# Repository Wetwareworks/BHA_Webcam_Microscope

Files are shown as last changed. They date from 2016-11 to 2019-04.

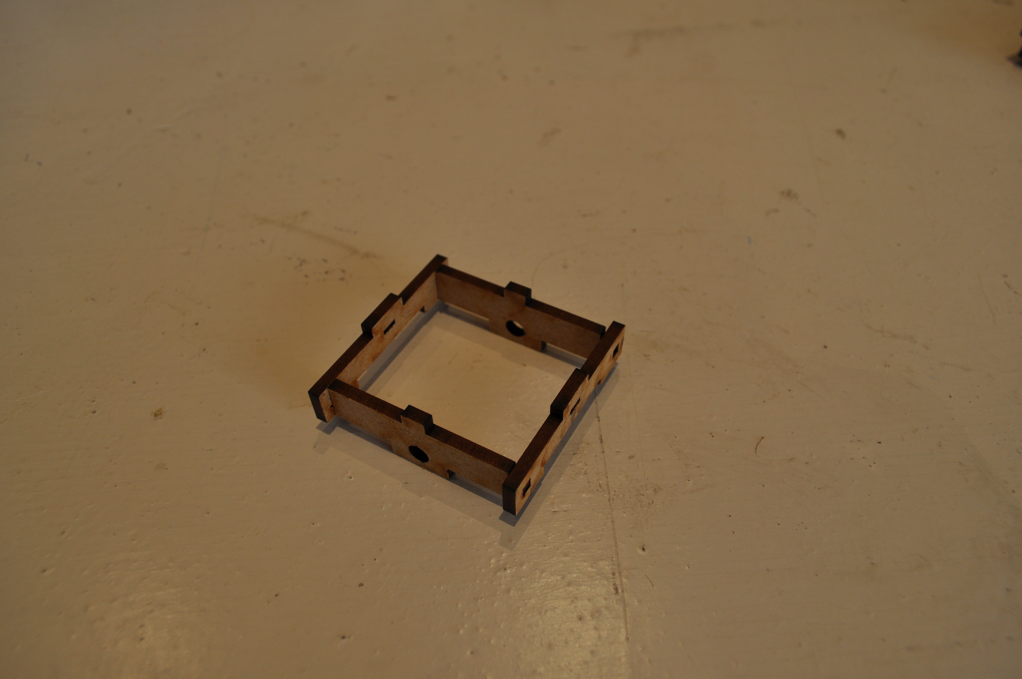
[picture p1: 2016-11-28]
Pictures/Assembly guide/DSC_0014.JPG

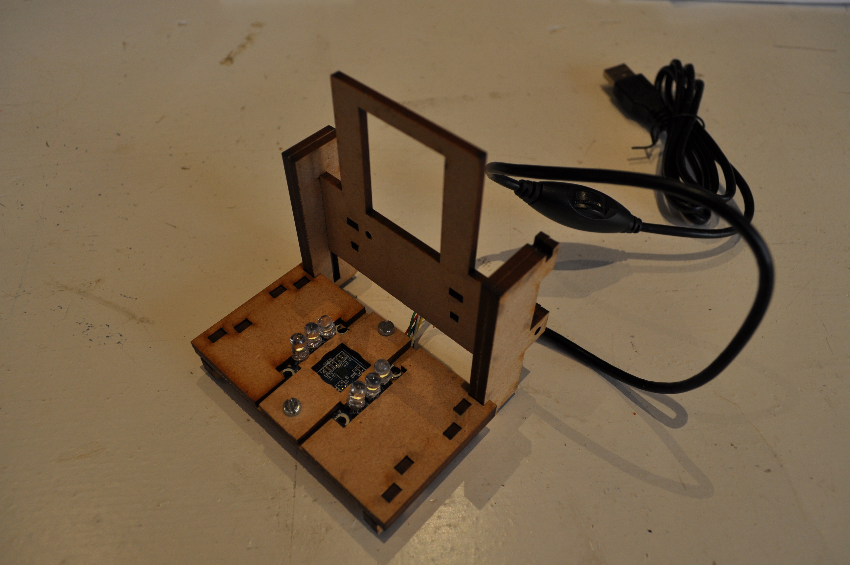
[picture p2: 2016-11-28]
Pictures/Assembly guide/DSC_0013.JPG

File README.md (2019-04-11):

# BHA Webcam Microscope

This repo contains the designs and source files of a **DIY Webcam Microscope**. This device can be used to observe microscope slides on your PC and play biotic games. 

On April 13, 2019 a workshop was conducted at the Mini Green Maker Faire Rhein-Waal. The assembly guide that was used there can be found in this repository as well.

## Navigation the repo

 	BHA_Webcam_Microscope/				Main repo
 	|-- Pictures/					Photo documentation
 	BoM.md						Bill of Materials
 	Webcam-Microscope-Assembly.pdf			Assembly guide
 	Webcam-Microscope-Biotic-Gaming-Fritzing.fzz	Wiring Scheme
 	Webcam-Microscope-Cut-Sheet.svg			Laser cut vector file
 	Webcam-Microscoep-Sketchup.skp			Sketchup 3D design
 	rpi-zero-w-video-streaming.md			Guide on setting up video streaming

## To Do

Please make more suggestions by posting in the Issues section of this GitHub Repo.

## License

All code is licensed under GNU General Public License.

All designs are licensed under Creative Commons Contribution Share-Alike license

## Credits

This design has been forked from Waag's Biohack Academy

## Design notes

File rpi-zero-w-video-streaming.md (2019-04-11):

# Raspberry Pi Zero W Video Streaming Guide

## Install Raspbian on your SD card

Follow the guide on http://www.raspberrypi.org for [Installing Raspbian on your SD Card](https://www.raspberrypi.org/documentation/installation/installing-images/README.md)

## Pre-configure Wifi and SSH settings on the SD card

Since we are going to use the Raspberry Pi "headless" (w/o keyboard, mouse or display) we will need to make some pre-configurations before booting up.

Create a file called "SSH" (without quotes and indeed without extension) in the BOOT partition of the SD card. This will enable SSH remote command line access once. The file is removed once Raspbian boots.

Create a file called "wpa_supplicant.conf" in the BOOT partition of the SD card, add the following:

```
country=[FILL IN YOUR TWO CHARACTER COUNTRY CODE e.g. US, DE, GB, NL]
update_config=1
ctrl_interface=/var/run/wpa_supplicant

network={
 scan_ssid=1
 ssid="PiScopeHub"
 psk="LetMeIn!"
}
```

Change the SSID of the network and psk password to whatever you need to connect to your Wifi.

## Configure Raspbian

Boot the Raspberry Pi by powering it up. Connect your computer to the same Wifi network and open up a SSH terminal.

```
### Open Raspbian configuration screen
sudo raspi-config
```

Under Network Options change the Hostname to e.g. PiScope1. This will make it easier to open up the video stream in your browser later on.

Under Interfacing Options enable SSH remote command line access permenantly.

Finish to save settings

## Install MJPG-streamer

```
# Update & Install Tools
sudo apt-get update
sudo apt-get upgrade -y
sudo apt-get install build-essential libjpeg8-dev imagemagick libv4l-dev cmake -y

# Clone Repo in /tmp
cd /tmp
git clone https://github.com/jacksonliam/mjpg-streamer.git
cd mjpg-streamer/mjpg-streamer-experimental

# Make
make
sudo make install

## Setup Management Script

```
sudo nano /home/pi/mjpg-streamer.sh

Add the below code to ( /home/pi/mjpg-streamer.sh )
```
#!/bin/bash

sleep 20 # wait for the RPi to finish boot

MJPG_STREAMER_BIN="/usr/local/bin/mjpg_streamer"  # "$(dirname $0)/mjpg_streamer"
MJPG_STREAMER_WWW="/usr/local/share/mjpg-streamer/www"
MJPG_STREAMER_LOG_FILE="${0%.*}.log"  # "$(dirname $0)/mjpg-streamer.log"
RUNNING_CHECK_INTERVAL="2" # how often to check to make sure the server is running (in seconds)
HANGING_CHECK_INTERVAL="3" # how often to check to make sure the server is not hanging (in seconds)

VIDEO_DEV="/dev/video0"
FRAME_RATE="3"
QUALITY="60"
RESOLUTION="480x320"  # 160x120 176x144 320x240 352x288 424x240 432x240 640x360 640x480 800x448 800x600 960x544 1280x720 1920x1080 (QVGA, VGA, SVGA, WXGA)   #  lsusb -s 001:006 -v | egrep "Width|Height" # https://www.textfixer.com/tools/alphabetical-order.php  # v4l2-ctl --list-formats-ext  # Show Supported Video Formates
PORT="8081"
YUV="yes"

################INPUT_OPTIONS="-r ${RESOLUTION} -d ${VIDEO_DEV} -f ${FRAME_RATE} -q ${QUALITY} -pl 60hz"
INPUT_OPTIONS="-r ${RESOLUTION} -d ${VIDEO_DEV} -q ${QUALITY} -pl 60hz --every_frame 2"  # Limit Framerate with  "--every_frame ", ( mjpg_streamer --input "input_uvc.so --help" )

if [ "${YUV}" == "true" ]; then
	INPUT_OPTIONS+=" -y"
fi

OUTPUT_OPTIONS="-p ${PORT} -w ${MJPG_STREAMER_WWW}"

# ==========================================================
function running() {
    if ps aux | grep ${MJPG_STREAMER_BIN} | grep ${VIDEO_DEV} >/dev/null 2>&1; then
        return 0

    else
        return 1

    fi
}

function start() {
    if running; then
        echo "[$VIDEO_DEV] already started"
        return 1
    fi

    export LD_LIBRARY_PATH="$(dirname $MJPG_STREAMER_BIN):."

	echo "Starting: [$VIDEO_DEV] ${MJPG_STREAMER_BIN} -i \"input_uvc.so ${INPUT_OPTIONS}\" -o \"output_http.so ${OUTPUT_OPTIONS}\""
    sudo ${MJPG_STREAMER_BIN} -i "input_uvc.so ${INPUT_OPTIONS}" -o "output_http.so ${OUTPUT_OPTIONS}" >> ${MJPG_STREAMER_LOG_FILE} 2>&1 &

    sleep 1

    if running; then
        if [ "$1" != "nocheck" ]; then
            check_running & > /dev/null 2>&1 # start the running checking task
            check_hanging & > /dev/null 2>&1 # start the hanging checking task
        fi

        echo "[$VIDEO_DEV] started"
        return 0

    else
        echo "[$VIDEO_DEV] failed to start"
        return 1

    fi
}

function stop() {
    if ! running; then
        echo "[$VIDEO_DEV] not running"
        return 1
    fi

    own_pid=$$

    if [ "$1" != "nocheck" ]; then
        # stop the script running check task
        ps aux | grep $0 | grep start | tr -s ' ' | cut -d ' ' -f 2 | grep -v ${own_pid} | xargs -r kill
        sleep 0.5
    fi

    # stop the server
    ps aux | grep ${MJPG_STREAMER_BIN} | grep ${VIDEO_DEV} | tr -s ' ' | cut -d ' ' -f 2 | grep -v ${own_pid} | xargs -r kill

    echo "[$VIDEO_DEV] stopped"
    return 0
}

function check_running() {
    echo "[$VIDEO_DEV] starting running check task" >> ${MJPG_STREAMER_LOG_FILE}

    while true; do
        sleep ${RUNNING_CHECK_INTERVAL}

        if ! running; then
            echo "[$VIDEO_DEV] server stopped, starting" >> ${MJPG_STREAMER_LOG_FILE}
            start nocheck
        fi
    done
}

function check_hanging() {
    echo "[$VIDEO_DEV] starting hanging check task" >> ${MJPG_STREAMER_LOG_FILE}

    while true; do
        sleep ${HANGING_CHECK_INTERVAL}

        # treat the "error grabbing frames" case
        if tail -n2 ${MJPG_STREAMER_LOG_FILE} | grep -i "error grabbing frames" > /dev/null; then
            echo "[$VIDEO_DEV] server is hanging, killing" >> ${MJPG_STREAMER_LOG_FILE}
            stop nocheck
        fi
    done
}

function help() {
    echo "Usage: $0 [start|stop|restart|status]"
    return 0
}

if [ "$1" == "start" ]; then
    start && exit 0 || exit -1

elif [ "$1" == "stop" ]; then
    stop && exit 0 || exit -1

elif [ "$1" == "restart" ]; then
    stop && sleep 1
    start && exit 0 || exit -1

elif [ "$1" == "status" ]; then
    if running; then
        echo "[$VIDEO_DEV] running"
        exit 0

    else
        echo "[$VIDEO_DEV] stopped"
        exit 1

    fi

else
    help

fi
```

## Enable start on Boot
```
# Make Executable
sudo chmod +x /home/pi/mjpg-streamer.sh

# Open Cron Job
sudo crontab -e

# Add line
@reboot bash /home/pi/mjpg-streamer.sh start
``````

### Credits

This guide has been derived from https://github.com/cncjs/cncjs/wiki/Setup-Guide:-Raspberry-Pi-%7C-MJPEG-Streamer-Install-&-Setup-&-FFMpeg-Recording

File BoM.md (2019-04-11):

## Bill of Materials

### Must have

We recommend to buy the cheapest webcam you can find. Most likely a similar model to [Eminent iCAM Webcamera](http://tweakers.net/pricewatch/275640/eminent-icam-webcamera-met-microfoon-(em1089).html) or [LogiLink Webcam USB with LED](http://tweakers.net/pricewatch/275550/logilink-webcam-usb-with-led.html). It is sold all around the world with different brands, but the internal electronics are the same.

Also, make sure you have enough 3mm material to cut the design from.

|No|Amount|Description|Supplier NL|Cost|
| ------------: | ------------: | :------------ | :------------ | ------------: |
|1|1|Webcam|[Conrad](https://www.conrad.nl/p/logilink-ua0072-webcam-640-x-480-pix-klemhouder-990561)|9.11|
|2|2|M3 16mm bolts|[Bevestigingsmateriaal.nl](https://www.bevestigingsmateriaal.nl/bevestigingsmateriaal/bouten-schroeven/buitenzeskant-kop/tapbouten-din-933/din-933-rvs-a2)||
|3|1|M3 10 mm bolt|[Bevestigingsmateriaal.nl](https://www.bevestigingsmateriaal.nl/bevestigingsmateriaal/bouten-schroeven/buitenzeskant-kop/tapbouten-din-933/din-933-rvs-a2)||
|4|3|M3 nut|[Bevestigingsmateriaal.nl](https://www.bevestigingsmateriaal.nl/bevestigingsmateriaal/moeren/zeskantmoer-din-934/din-934-rvs-a2)||
|5|1|5mm White LEDs|[iPrototype](https://iprototype.nl/products/components/led-lcd/ledwit), [EOO](https://www.eoo-bv.nl/led-5-mm/9088-ml5fw13h.html), [Hackerstore](https://www.hackerstore.nl/Artikel/257)|0.18|
|6|4|3mm White LEDs|[Farnell](http://nl.farnell.com/multicomp/ovl-3321/led-3mm-bright-white-8cd/dp/1716696)|0.45|
|7|5|220 ohm resistors|[Hackerstore](https://www.hackerstore.nl/Artikel/478), [Farnell](http://nl.farnell.com/multicomp/mcf-0-25w-220r/resistor-carbon-film-220r-0-25w/dp/9339299?Ntt=9339299), [iPrototype](https://iprototype.nl/products/components/resistors/220R), [EOO](https://www.eoo-bv.nl/metaaloxide-3w/7085-metaalox-3w-220.html)|0.02|

It terms of controlling the LEDs or streaming the video footage there are multiple options. The simplest solution is to use an Arduino or similar microcontroller. A more advanced option is to use a Raspberry Pi to not just control the LEDs via the GPIO pins, but also stream the video footage over wifi. A guide on how to configure a Raspberry Pi Zero W for video stream can be found here [Raspberry Pi Zero W video streaming guide](/rpi-zero-w-video-streaming.md).

### Optional Arduino

|No|Amount|Description|Supplier NL|Cost|
| ------------: | ------------: | :------------ | :------------ | ------------: |
|1|1|Arduino|[Hackerstore](https://www.hackerstore.nl/Artikel/17)|9.95|

### Optional Raspberry Pi

|No|Amount|Description|Supplier NL|Cost|
| ------------: | ------------: | :------------ | :------------ | ------------: |
|1|1|Raspberry Pi Zero W|[Kiwi](https://www.kiwi-electronics.nl/raspberry-pi-zero-w)|11.00|
|2|1|Micro USB power adapter|[Mini In The Box](https://www.miniinthebox.com/nl/p/thuislader-draagbare-lader-telefoon-usb-oplader-europese-stekker-snellader-qc3-0-1-usb-poort-2a-ac-100v-240v_p6441178.html)|4.50|
|3|1|Micro-USB OTG cable|[AlleKabels](https://www.allekabels.nl/usb-otg-kabel/6300/1258217/usb-micro-otg-kabel.html)|2.95|
|4|1|8 GB micro SD card|[Reichelt](https://www.reichelt.nl/microsdhc-geheugenkaart-16gb-canvas-select-sdcs-16gb-p227499.html)|3,56|

You will also need:

* Some wood glue
* Maybe some tape
* Screw driver

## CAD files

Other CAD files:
Archive/2015 BHA1/Webcam-Microscope-Sketchup.skp
Archive/2015 BHA2/Webcam-Microscope-Sketchup.skp
Archive/BHA1/Webcam-Microscope-Sketchup.skp
BHA2-Webcam-Microscope-Sketchup.skp
Webcam-Microscope-Sketchup.skp

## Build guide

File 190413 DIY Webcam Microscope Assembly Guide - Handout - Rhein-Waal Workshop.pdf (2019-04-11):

DIY Webcam Microscope Assembly Guide | 10‐4‐2019

# DIY Webcam Microscope

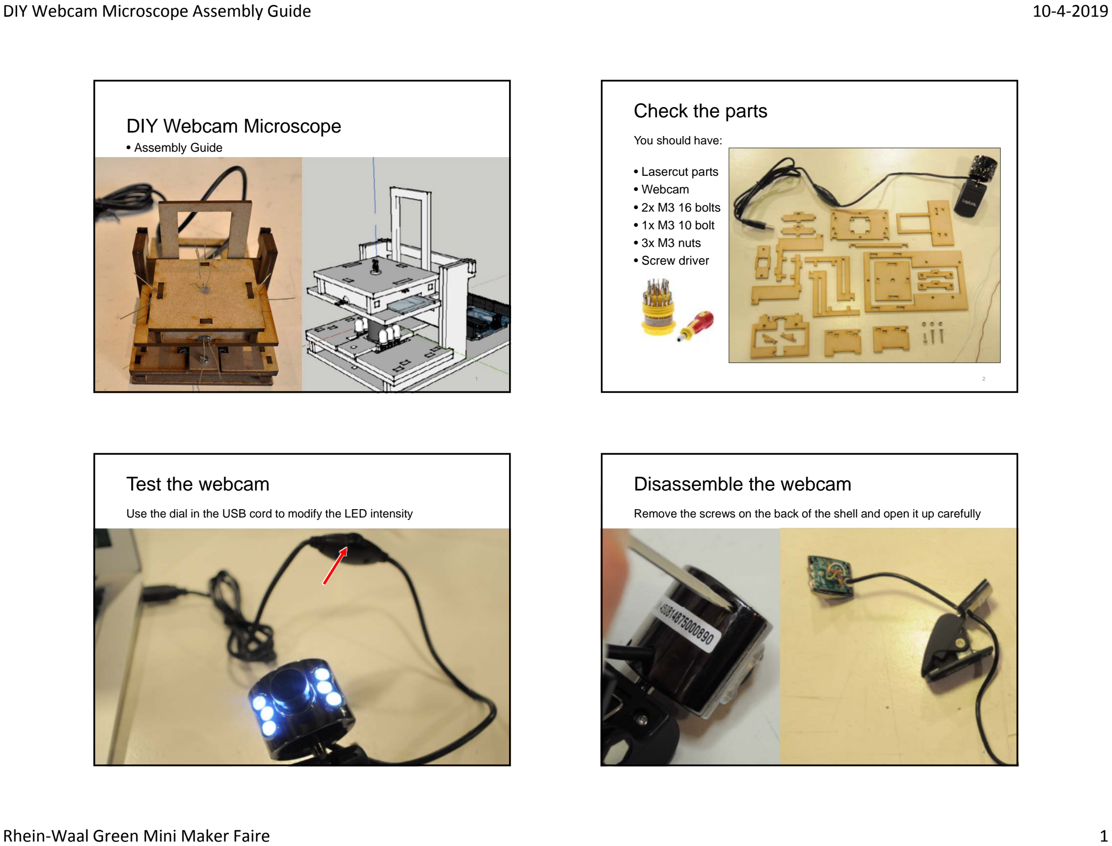
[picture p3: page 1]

Rhein‐Waal Green Mini Maker Faire | 1
- Assembly Guide

1

# Check the parts

2

- Lasercut parts
- Webcam
- 2x M3 16 bolts
- 1x M3 10 bolt
- 3x M3 nuts
- Screw driver

You should have:

# Test the webcam

Use the dial in the USB cord to modify the LED intensity

3

# Disassemble the webcam

Remove the screws on the back of the shell and open it up carefully

4

# Unscrew the lens by turning it

# Remove the lens holder

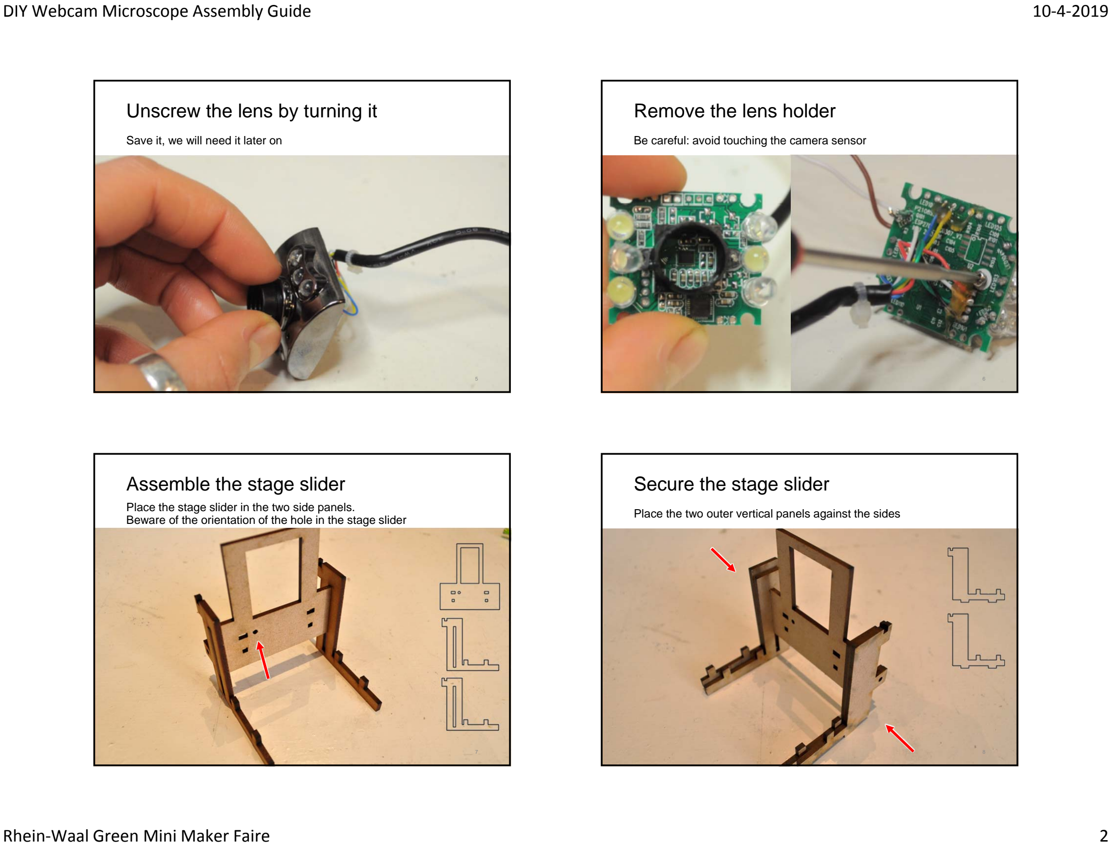
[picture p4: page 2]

Save it, we will need it later on

5

Be careful: avoid touching the camera sensor

6

# Assemble the stage slider

Place the stage slider in the two side panels.
Beware of the orientation of the hole in the stage slider

7

# Secure the stage slider

Place the two outer vertical panels against the sides

8

# Attach the camera mount

# Push the PCB through the panel

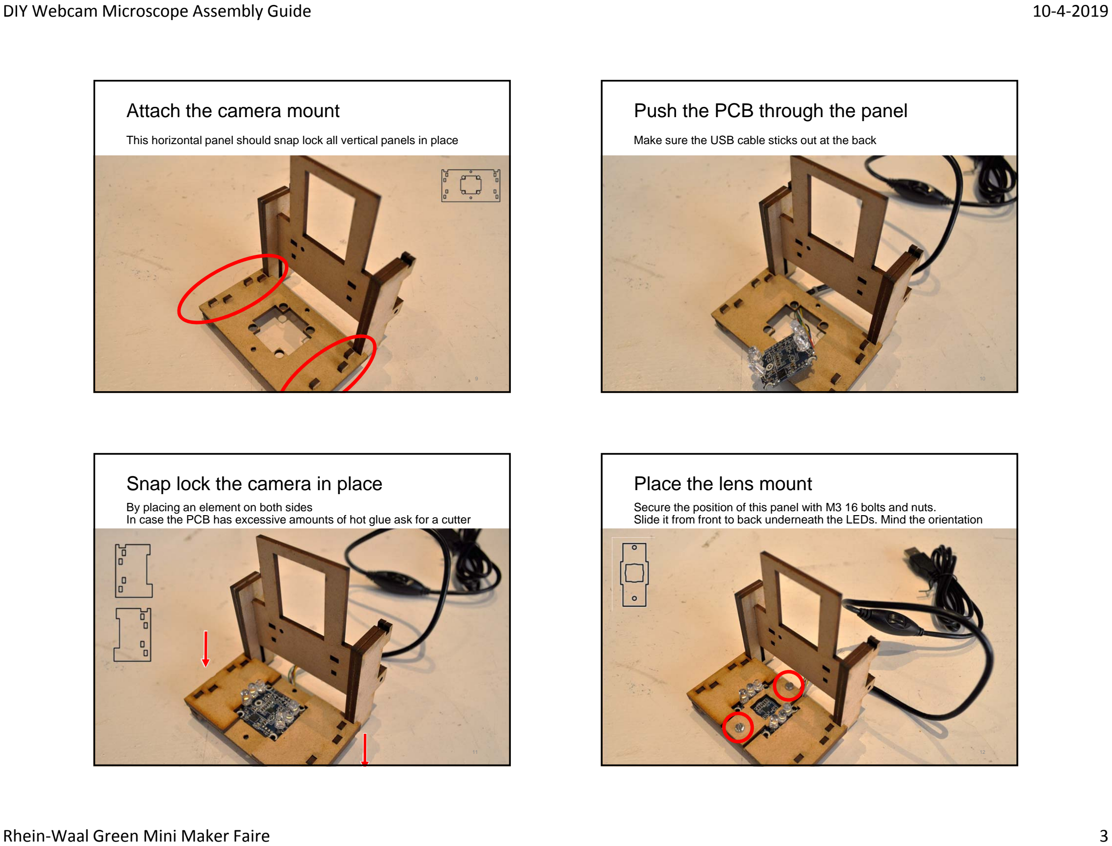
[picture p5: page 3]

This horizontal panel should snap lock all vertical panels in place

9

Make sure the USB cable sticks out at the back

10

# Snap lock the camera in place

By placing an element on both sides
In case the PCB has excessive amounts of hot glue ask for a cutter

11

# Place the lens mount

Secure the position of this panel with M3 16 bolts and nuts.
Slide it from front to back underneath the LEDs. Mind the orientation

12

# Assemble the stage lid

# Mount the four LEDs

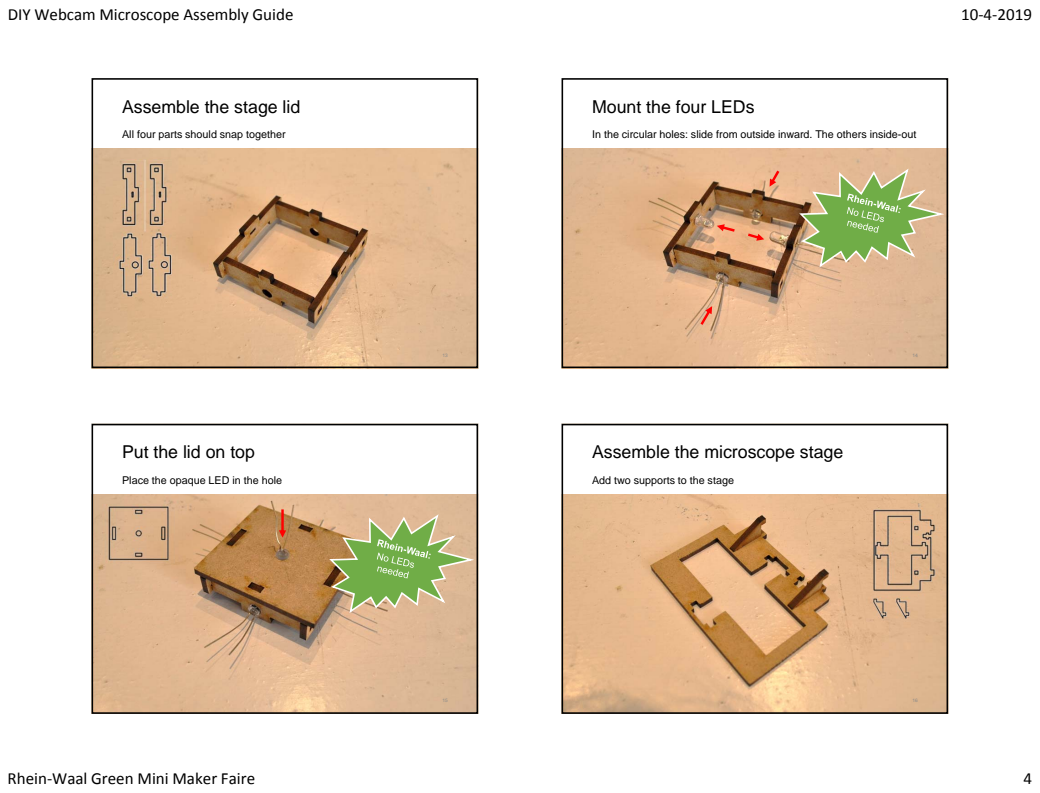
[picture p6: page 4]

All four parts should snap together

In the circular holes: slide from outside inward. The others inside-out

Put the lid on top

Assemble the microscope stage

Place the opaque LED in the hole

Add two supports to the stage

# Attach the stage to the slider

# Put the lens in place

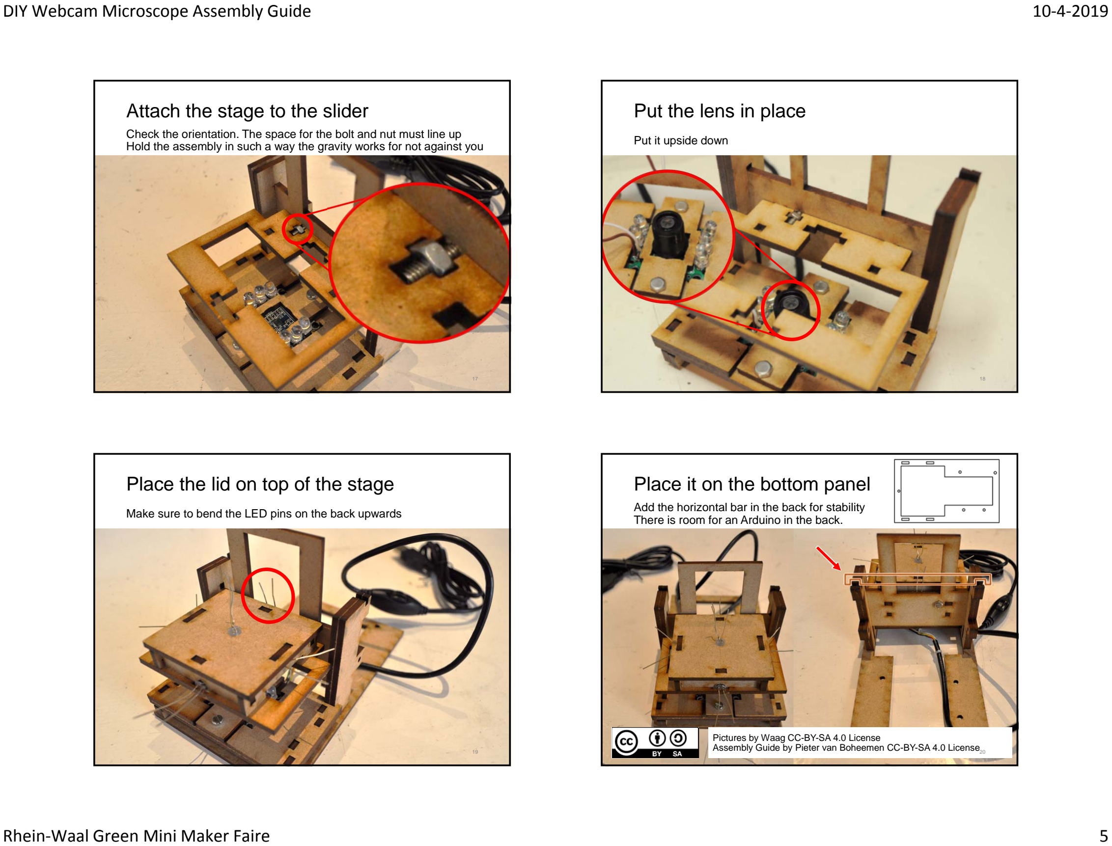
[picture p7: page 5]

Check the orientation. The space for the bolt and nut must line up Hold the assembly in such a way the gravity works for not against you

17

Put it upside down

18

# Place the lid on top of the stage

Make sure to bend the LED pins on the back upwards

19

# Place it on the bottom panel

Add the horizontal bar in the back for stability There is room for an Arduino in the back.

Pictures by Waag CC-BY-SA 4.0 License
Assembly Guide by Pieter van Boheemen CC-BY-SA 4.0 License20

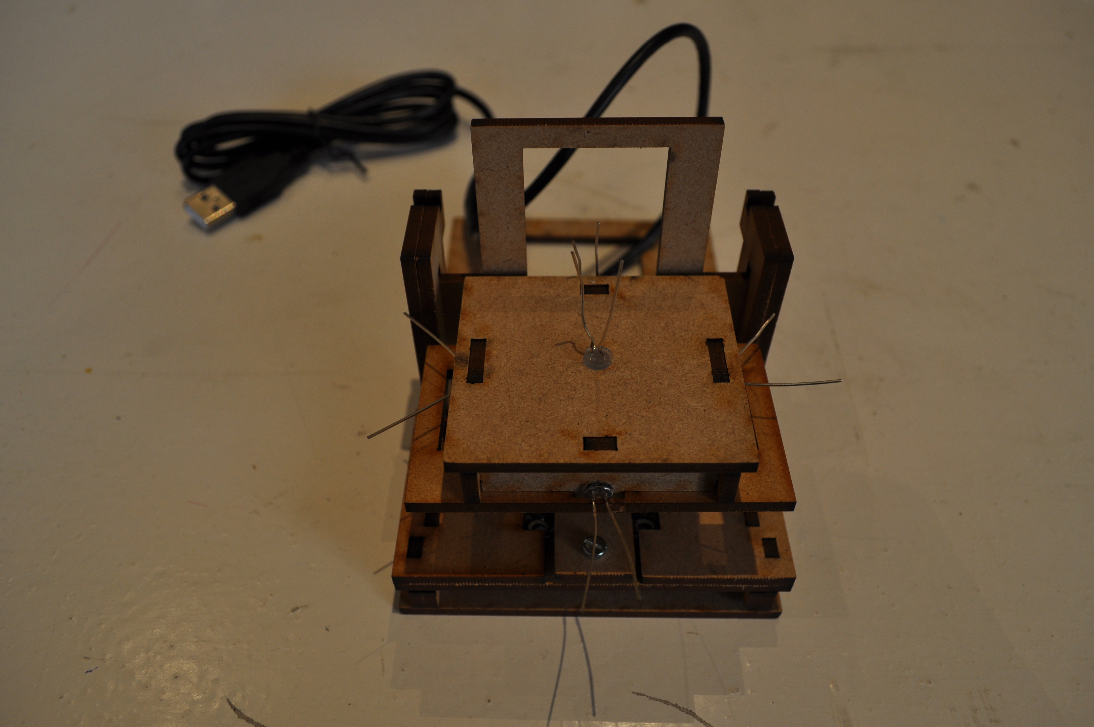
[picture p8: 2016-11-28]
Pictures/Assembly guide/DSC_0030.JPG

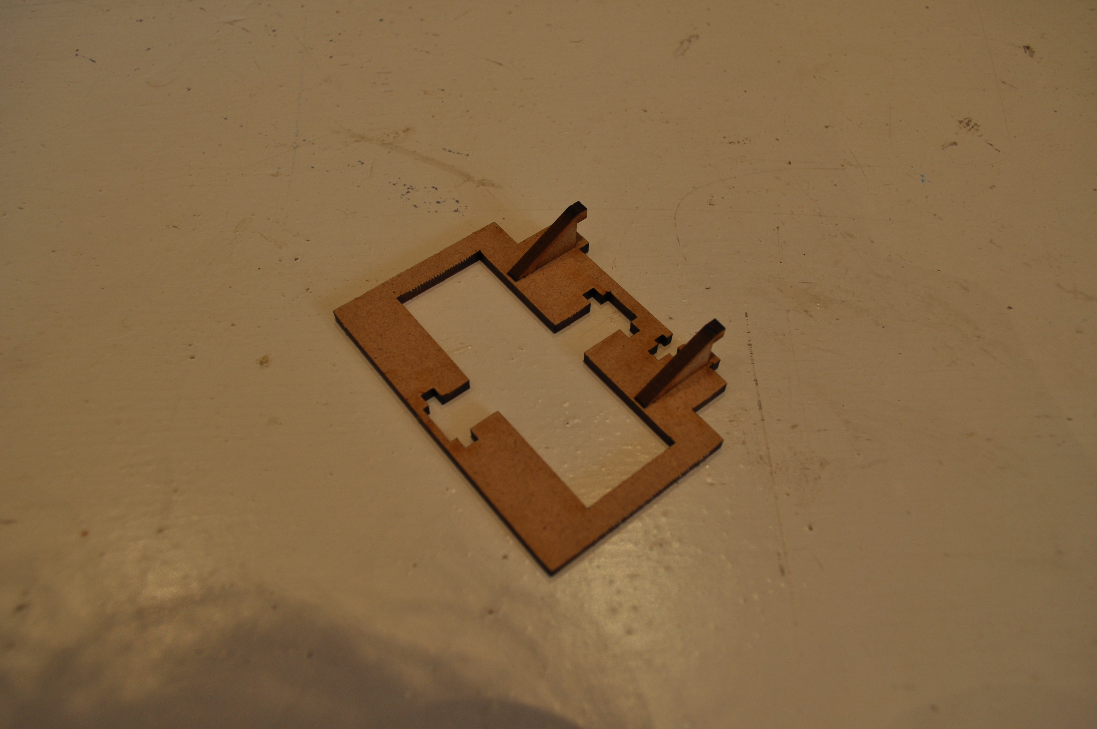
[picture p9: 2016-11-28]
Pictures/Assembly guide/DSC_0018.JPG

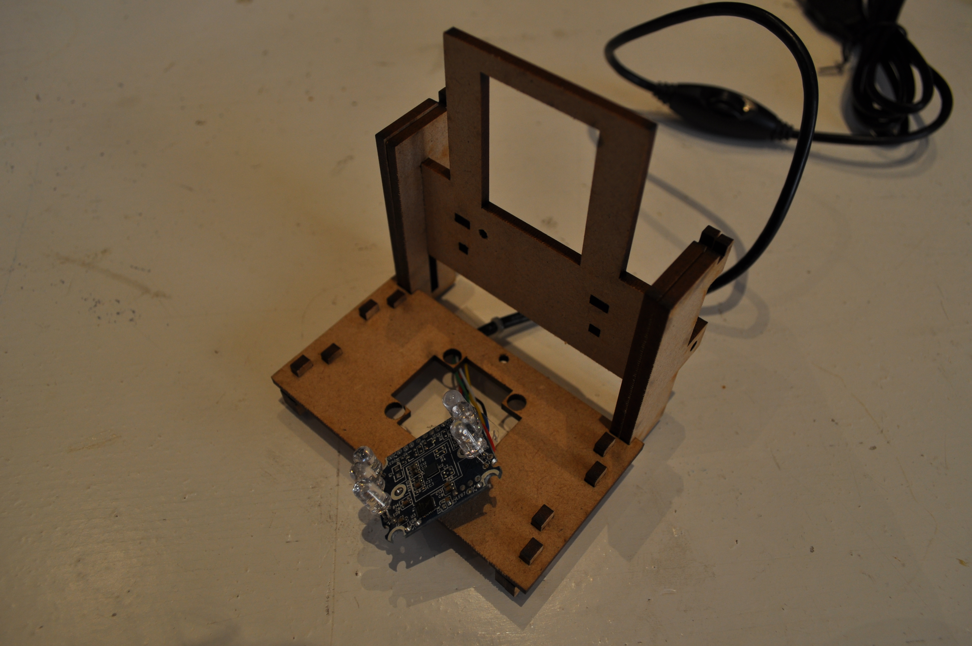
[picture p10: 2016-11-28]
Pictures/Assembly guide/DSC_0007.JPG

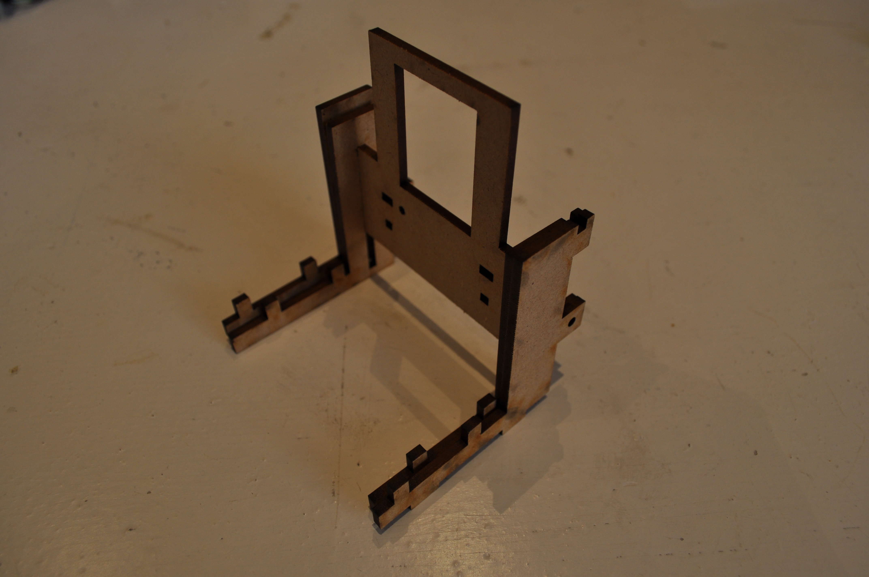
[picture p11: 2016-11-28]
Pictures/Assembly guide/DSC_0004.JPG

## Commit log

2015-06-30 Archive BHA1
    [Webcam-Microscope-Sketchup.skp]
2015-07-21 Updated Sketchup file, including camera mount
    [BHA2-Webcam-Microscope-Sketchup.skp]
2016-02-16 update pictures
    [Webcam-Microscope-Sketchup.skp]
2016-10-27 BHA4 design
    [Webcam-Microscope-Sketchup.skp]
2016-12-16 BHA4 update
    [Webcam-Microscope-Biotic-Gaming-Fritzing.fzz]
2019-04-11 Add files via upload
    Assembly guide for the DIY Microscope workshop at the Mini Green Maker Faire Rhein-Waal on April 13th, 2019
